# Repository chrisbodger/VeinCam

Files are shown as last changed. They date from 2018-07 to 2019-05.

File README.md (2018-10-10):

# Table Of Contents
1. [Feedback](#1-feedback)
2. [Progress Update](#2-progress-update)
3. [Audit Log](#3-audit-log)
4. [Concept of Operations](#4-concept-of-operations)
5. [Meeting Minutes](#5-meeting-minutes)
6. [Design Documents](#6-design-documents)

# 1. Feedback
A feedback form has been created for the interest of our stakeholders, should they wish to pass on any changes or improvements they believe to be prudent. The form can be found [here](https://goo.gl/forms/8cw5eWdaOY5C1jBo1).

Once the feedback has been received, an issue will be created within the GitHub repository for public viewing and tracking.  
**Any feedback is welcome.**

# 2. Progress Update
## October 9th

### Software

Implimented buttons into the HTML video streaming page, which trigger Flask/Python functions to set the camera parameters of brightness, contrast and saturation for the next frame. These buttons were designed to be large and use appropriate colours (red for lower, green for higher) in order to be intuative and intended for an educational audience. Following a meeting with the client after the testing, the stream is now shown in portrait rather than landscape to take advantage of the fact most users will be streaming to their personal devices in a portrait orientation, as well as being able to view someone's arm verticaly along the webpage.

All code had been uploaded into the software folder, including a complete image file which can be written to an SD card and used immediately with a Raspberry Pi and a PiCam (a method which has been tested and validated!). If the user does not have a PiJuice shield, minor adjustments must be made to app.py (see README.md in software folder or /home/pi/pistream in image for details).

#### A chronological work diary of software development throughout this project has also been added to the software folder.

### Audit 3 Presentation

The VeinCam was presented at our final Audit presentation during our tutorial timeslot. The final version was demonstrated to shadows and tutor. A draft of the poster to be presented next week was shown for feedback. The feedback given on the physical design, product functionality and overall presentation was very positive.

## Previous Progress Updates
* [August 1st](Progress-Updates/progress-update-2018-08-01.md)
* [August 7th](Progress-Updates/progress-update-2018-08-07.md)
* [August 11th](Progress-Updates/progress-update-2018-08-11.md)
* [August 18th](Progress-Updates/progress-update-2018-08-18.md)
* [August 25th](Progress-Updates/progress-update-2018-08-25.md)
* [September 5th](Progress-Updates/progress-update-2018-09-05.md)
* [September 25th](Progress-Updates/progress-update-2018-09-25.md)
* [October 2nd](Progress-Updates/progress-update-2018-10-02.md)

## Work Diary
For more detailed information on the work that has been completed please refer to the [work diary](docs/Team-Work-Diary.md)

# 3. Audit Log
Here we will have the information, results, and feedback to our audits, and will be presented in the following links (as they are created):

* Audit 1
* Audit 2
* Audit 3

Should our stakeholders wish to provide us with feedback, they can fill out a google survey in which we will action them appropriately as responses are presented to us.

# 4. Concept of Operations
Our Concept of Operations has undergone further iterations in recent weeks, primarily to the aims, scope and stakeholders of the project. We encourage any feedback on changes made.

The [Concept of Operations](docs/CONOPS.md) document can be found in our repository.

# 5. Meeting Minutes
Team meetings are scheduled two to three times a week with different stakeholders present. One meeting is internal with only the project team, one has the tutor and shadow team present, and one is with the project client. They are currently scheduled for the following times:
* Tuesday 10am (Tutor and Shadow Team)
* Wednesday 11pm (Project Team)
* Saturday 2pm (Project Client)

The wednesday and saturday meeting times may vary, depending on the availability of the team, and client.

Meeting Minutes can also be found in our repository:

## Last Meeting Minutes
* [September 29th](Meeting-Minutes/Meeting-Minutes-2018-09-29.md)

## Recent Meeting Minutes
* [September 5th](Meeting-Minutes/Meeting-Minutes-2018-09-05.md)  
* [September 15th](Meeting-Minutes/Meeting-Minutes-2018-09-15.md)
* [September 18th](Meeting-Minutes/Meeting-Minutes-2018-09-18.md)
* [September 19th](Meeting-Minutes/Meeting-Minutes-2018-09-19.md)
* [September 22nd](Meeting-Minutes/Meeting-Minutes-2018-09-22.md)

# 6. Design Documents
The design of the VeinCam will be presented here, once the ConOps has been approved, and progress/final designs are made available. the construction method of the device will also be presented here.

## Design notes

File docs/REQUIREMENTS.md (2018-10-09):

# Device Requirements and Design Specifications
Requirements were gathered from the client and refined into measurable specifications. The sets of both requirements and specifications should be considered evolutionary and may change through prototyping and testing.

## Requirements
Requirements have been developed through conversation with the project client resulting in a total of eight that would make the VeinCam a success.

| ID | Requirement |
| --- | --- |
| 1 | The device must be inexpensive compared to devices that have similar functions |
| 2 | The device must be handsfree |
| 3 | The device must be able to wirelessly connect to an external device with a screen |
| 4 | The device must be portable and mobile |
| 5 | The device must be simple to use |
| 6 | The device must be simple to construct |
| 7* | The device must display veins in as many use-cases as possible (e.g dark-skinned, tattooed, hairy) |

*Requirement 7 has elements of a stretch deliverable for the project.

## Specifications
The requirements were broken down into specifications that will provide validation for the project and can be verified through testing.

| ID | Specification | Metric | Benchmark |
| --- | --- | --- | --- |
| 1 | Total Cost | $ | <250 |
| 2.1 | Camera Focal Length | mm | 300-500 |
| 2.2 | Adjustable Set Height | mm | 300-500 |
| 2.3 | Handsfree Operation | min | >5 |
| 2.4 | Battery Life | min | >60 |
| 3.1 | Wireless Range | m | >1 |
| 3.2 | Stream Delay | ms | <1000 |
| 4 | Form Factor | mm | <150 x 90 x 70 |
| 5.1 | User Acceptance | % | >90 |
| 5.2 | Boot Time | s | <15 |
| 5.3 | OS Compatibility | # | >2 |
| 6.1 | Construction Steps | # | <5 |
| 6.2 | Construction Time | hrs | <2 |
| 7.1 | Automatic Contrast Adjustment (for ideal scenario) | % | >90 |
| 7.2 | Automatic Contrast Adjustment (for any complexion) | % | 80 |
| 7.3 | Automatic Contrast Adjustment (for high BMI/obesity) | % | 80 |
| 7.4 | Automatic Contrast Adjustment (for any amount of hair) | % | 80 |
| 7.5 | Automatic Contrast Adjustment (for tattooed area) | % | 80 |
| 7.6 | Visualise Vascular Blood Flow | % | 80 |

### Description
**1. Total Cost -** The total cost of all components necessary to construct the VeinCam

**2.1. Camera Focal Length -** The focal length of the camera used in the device. Must have an image in focus at a height where it will not interfere with the users.

**2.2. Adjustable Set Height -** The heights that the device can be held still without human interaction once set in the appropriate position (i.e within the camera focal length).

**2.3. Handsfree Operation -** The time that both the physical device and the software interface can operate without human interaction.

**2.4. Battery Life -** The amount of time the device can be used (while streaming) without needing to be plugged in to recharge.

**3.1. Wireless Range -** The range that the device is able to communicate wirelessly with an external device.

**3.2. Stream Delay -** The time taken for the recorded image to be processed and appear on the external device.

**4. Form Factor -** The size and shape of the device.

**5.1. User Acceptance -** The success rate that the device with users. Measured by user testing and feedback.

**5.2. Boot Time -** The time taken from switching the device on to an image being produced.

**5.3. OS Compatibility -** The number of operating systems that the device is compatible with.

*Note - More specifications may be generated for Requirement 5 after initial testing.*

**6.1. Construction Steps -** The number of steps needed to construct the device from scratch.

**6.2. Construction Time -** The time taken for an independent user to construct the device from scratch. To be tested by independent users.

**7.1-5. Automatic Contrast Adjustment (for various use cases) -** The success rate of the device to automatically adjust the contrast of the streamed image such that veins can be clearly seen, as judged by the user. Ideal situation is with a patient with a light complexion, against a white background. Other scenarios are where vein detection has been shown to be more difficult.

**7.6. Visualise Vascular Blood FLow -** The ability of the device to visualise real-time blood flow. Measured through success rate in user testing.

## Change Log

| Date | Section | Change | Justification |
| --- | --- | --- | --- |
| 26/9/18 | [Requirements](#requirements) | Remove sterilisation requirement and associated specifications: gapless case and surface roughness. | The device is to be used as an educational tool as opposed to a medical device. |
| 26/9/18 | [Requirements](#requirements) | The device does not need to improve venous puncture but still work for as many use cases as possible | As above. |
| 29/9/18 | [Specifications](#specifications) | Moved automatic contrast adjustment (ideal scenario) to requirement 7. | Testing has to be split up between device and user, this groups more user testing together. |

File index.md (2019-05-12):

<meta http-equiv="refresh" content="0; URL='http://chrisbodger.github.io/veincam2019'" />

<!--

<div style="text-align:center"><img src ="images/progress-images/test-stream-result-3-crop.png" /></div>

## What is the VeinCam
The VeinCam is an educational tool for vein visualisation that uses. It uses near infrared (nIR) light and a camera to stream a real-time image where veins can be easily seen. It is an open-source, build-it-yourself device so anyone who finds it useful will be able to construct it. There is a how-to guide of what materials to buy, how to put them together and the software to upload to get it all working.

## Current Stage
The VeinCam has been through a couple of prototypes to get to its current stage; which includes a functioning case, automatic image processing and manual controls on a streamed webpage. The current prototype looks absolutely stunning along side our favourite houseplant, Hugh!

<div style="text-align:center">
  <div class="row">
    <div class="column">
      <img src ="images/prototype/prototype-2.2-down.JPG" width="99%" height="99%">
    </div>
    <div class="column">
      <img src ="images/prototype/prototype-2.2-up.JPG" width="99%" height="99%">
    </div>
  </div>
  <div class="row">
    <div class="column">
      <img src ="Software/tutorial-images/iPhone Mockup1.png" width="99%" height="99%">
    </div>
    <div class="column">
      <img src ="Software/tutorial-images/iPhone Mockup2.png" width="99%" height="99%">
    </div>
  </div>
</div>

### To contribute or find out more check out the [GitHub site](https://github.com/chrisbodger/VeinCam) or email at <message2ben@gmail.com>
--!>

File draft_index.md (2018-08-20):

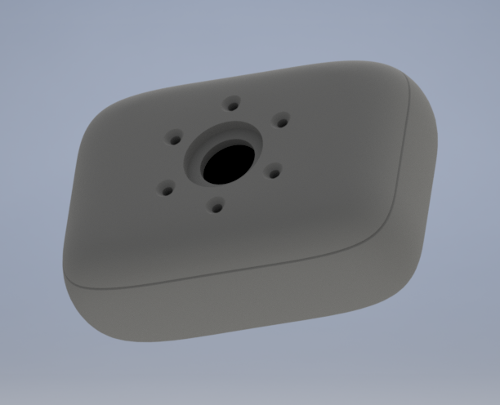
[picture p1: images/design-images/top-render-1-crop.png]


# What We're Doing
The main goal of our project is to ease patient discomfort. To do this we're using the VeinCam to make it easier for medical professionals to see veins in patients for superficial venous puncture.

# How We're Doing It
Not only are we making it easier, we're giving the power to them by developing an open-source DIY VeinCam and how-to guide so that anyone who needs one can build it themselves. We're providing a guide of what to buy, how to put it together and the software to upload to get it all working.

# When We're Done
This page will provide all the necessary downloads, links and resources that you'll need to construct a VeinCam yourself.

# Where We're At Now
Right now we're still working on getting it up and running but we have an image from our setup (as you can see we're using [Raspberry Pi](https://www.raspberrypi.org/) materials as they're available all over the world):

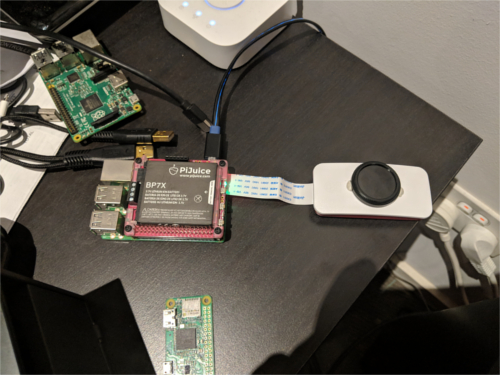
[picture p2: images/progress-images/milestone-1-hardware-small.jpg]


Our latest tests have been giving us some pretty good results as you can see below, but we're still working on adding automatic and manual contrast adjustment as well as a few other features.

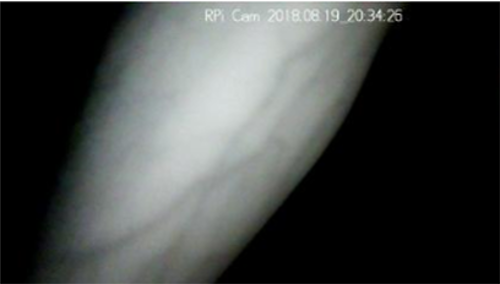
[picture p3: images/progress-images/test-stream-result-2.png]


## For more details check out our [GitHub site](https://github.com/chrisbodger/VeinCam)

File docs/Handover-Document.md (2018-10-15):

# Handover Document

This document is intended for the use of the Client Ben Healy, for future project teams who are continuing with this project in future semesters, and members of the public who wish to view the development and progress of the project summarised as of November 2018.

Feedback on this document, development of the project and other aspects of the project repository is always welcome and will be directed to the current project team FEEDBACK LINK HERE

Person's of interest for this document
'Client' - Ben Healy, medical student at the Australian National University
'Project Team'

## 1. Aims and purpose of this project
This project was started by the client who wished to develop an accessible and low-cost device that could be developed for the public for the purpose of enhanced vein visualisation using infra-red light - the VeinCam.
The client developed a preliminary prototype of the VeinCam based on the 2017 HackADAy Venenfinder project, and passed this prototype onto the project team to complete for their university course for further development of the device.
A full list of the project goals and stretch goals are in the [Concept of Operations document (ConOps)](/docs/CONOPS.md).

The project team is a group of four undergraduate ANU Engineering Students who completed a course which involved development of something as per the requirements and directions of the client. The course began in July 2018 and completed in November 2018.
A full list of the relevant stakeholders and their responsibilities at this stage of the project are
in the[ConOps](/docs/CONOPS.md).

The requirements developed by the project team and agreed upon by the client are listed in detail in the [Requirements](/docs/REQUIREMENTS.md)

## 2. Key development milestones and decisions
Decisions are summarised only in this document, with full dates, stakeholders involved and justifications in the [Decision Log](/docs/Decision-Log.md)
Main milestones are summarised in this document, with more details day-to-day activities in the [Team Work Diary](/docs/Team-Work-Diary.md)
Project updates have also been included in the repository every couple of weeks LINK HERE

### 2.1. Software development, key milestones and decisions
**Image Processing**
Currently, the VeinCam performs a histogram equilisaiton to "flatten" the contrast range of a taken image. This allows veins to not be washed out by higher contrast pixels of the image and as a result, veins appear are more prominently. There are several other image processing techniques that would be worth exploring to improve the VeinCam. These would include grayscaling, brightness/contrast threshold techniques, colour profiling and further histogram equilisation adjustment. Such examples can be found here:
https://hackaday.io/project/26158-assistance-system-for-vein-detection/details
https://hackaday.io/project/13329-yet-another-ir-vein-detector/details

**Manual Adjustment and Web Interface**
Following our final Audit, feedback was given on the ergonomics of the user web interface. It was mentioned that the buttons which manually adjust the brightness, contrast and saturation are not really suited beneath the image and having to continually scroll down is something that could be improved upon. A recommended solution for this would be a hidden sliding/three bar menu (as seen on many mobile websites) which would reveal the buttons to make adjustments to the stream.

The manual adjustment requires more manual testing to see what ranges and what parameters are best to adjust. The level of equalisation was also a parameter that was to be modified but the active decision was made to only adjust brightness, contrast and saturation as a proof of concept. There are many more possible parameters to adjust, including the levels of colour/brightness thresholds and strength of other imaging techniques, as well as being able to switch the image techniques being shown on the stream. 

### 2.2. Hardware development, key milestones and decisions
**Case**
The final case that we printed before the end of the project had some slight errors - namely misaligned buttons and LED passthroughs. We were able to overcome this defects for testing and demonstration purposes however. The repository contains v2.3 that includes these changes, and needs to be printed and tested going forward.

A proper mounting and securing solution needs to be designed for the Raspberry Pi, to prevent it from falling out of the case was it is being used. Currently, we are using foam cut-outs that were lodged in between the Pi and the case and that secured it quite well, though its not very permanent.

Because of the cut-outs, the device case is not very resistant to any sort of fluid. Some method needs to be implemented to plug these holes temporarily (a charging port cover for example), or permanently (LED indicator passthroughs). Transparent filament could be used and printed in situ to create a light channel for the LED lights and make them easier to see from the external of that case (a traditional method for indicator lights in devices), or use some other material like clear acrylic sheet and stuff it into the holes. Both options worth exploring.

The buttons are complete and should fit snuggly into the button holes.

**Surface Finish**
We were not able to perform any post-printing methods to clean up the prints. We were left with bumps and misplaced filament and an excess of support material to be removed still. This could be potentially detrimental as it leaves the case to be able to pick up dirt and grime and dirty up the case and potentially encourage bacterial growth given the number to small crevices within the surface. An idea that was had was to sand down the external surfaces with a fine grit to smooth it down, and adjust the print settings for the support material. other options could be utilised, depending on how the case is made.

In addition, not many people may have access to 3D printers. It would be worth looking into alternative case ideas, such as cardboard (like the Google Cardboard or Nintendo Labo), or acrylic sheet.

**IR LED Array**
The LED array was always intended to have its own custom PCB, to make it easier to manufacture as it would remove some variances of soldering the LEDS incorrectly and still fitting within our case design.

**Pi Zero Platform**
Given the resources used while the camera stream was operating, it may be possible to downsize the Pi 3 to a Pi Zero. This could potentially decrease the battery usage, and make appropriate use of the available resources, instead of having so much not utilised. This would still need to be tested of course, something we wished to at least attempt. But we did not have any interfacing methods to at least connect the Pi to a network, let alone connect the camera module to the Pi Zero.

The bottleneck with both Raspberry Pis would be the number of devices connected via the hotspot software. We experienced a lockup of the device when more than eight devices tried to connect during our presentation. However, given that only one device should be connected the the Pi at any given time, this should not be an issue going forward.

### 2.3. Governance and project aims/scope, key milestones and decisions

## 3. Future of the Project
Ideas about the future of include things that this project team has attempted and needs improvement on, things which were
outside the scope of the project (either from the beginning, or later on in the project).
These ideas were developed from the project team, with external advice and feedback from the client.
Testing that was completed by the client just prior to the end of the project is summarised in [this document](/Resources/Client-Feedback-VeinCam-Testing.md).

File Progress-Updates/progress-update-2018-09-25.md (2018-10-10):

## September 25th
Several weeks have gone by since the last update, and theres much to talk about:

### Hardware
We are up to case version 2.2, that incorporates a smaller form factor and better ergonomics. Unfortunately these past few weeks have not been able to produce a successful print of the new case. We believe that this will be the final iteration of the case.

The only variation to the case that may happen is testing into a different LED configuration. the aim is to attempt to achieve a better contrast of skin and veins, and hope to achieve deeper skin penetration to visualise veins on people who have a higher BMI. This is still on going but we hope to have a clear idea by the end of this week.

### Software
The software currently works to automatically start up on boot up; initialising the wireless access point for external connections and starting the web stream to an external device. It has been noted that the wireless access point fails to start sometimes, making it difficult to connect to externally. This will be looked into as it is believed that there is other software that may be interfering with the hosting software and blocking it from starting.

Aside from this, some manual controls will be implemented to the hosting web page for better control over the software processing and image input.

### Governance and Bureaucratic Issues
Over the source of the mid semester teaching break the team was in contact with a variety of sources to discuss the purpose of the device and how that impacts the how we distribute information about the device. Through much discussion, the group decided the best path for the future of the project would be to advertise the device as an educational tool, assisting with teaching about veins and educating the public for informed consent of medical procedures.

Additionally, through correspondence with legal services and the ANU Human Ethics Committee, the group became aware that initial human testing of the device would not be able to be completed at this stage of the project as human ethics approval is necessary to do testing. This provides some roadblocks for the development of the device as the group is not able to determine how the device needs to be improved for optimal practical use. As such, the aims and scope of the project were modified slightly.

Going forward, the group will be finishing up with tutorial documents on how to build the device, documents for conducting future testing, and acting on feedback from the client on the functioning of the device. The group is also developing designs for the poster to present the device at the closure of this project.

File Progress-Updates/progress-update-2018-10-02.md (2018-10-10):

## October 2nd
The client has recieved our second complete prototype to take and provide feedback on based on their use.
Photos of the prototype can be found in the 'images' folder, and a user instructions manual above in the main respository.  

### Hardware
At long last, case version 2.2 finally completed a full successful print. No changes were made to the LED configuration after testing of LEDS with differing wavelengths (840 vs 940nm) proved to not improve performance of viewing veins. The case was assembled however the mounts, charging port and button hole placement was found to be all out of place (less so than previous iterations). This will be a major focus for the final design.

Instead, firm packing foam was used to hold the components in place and align the PiJuice charging port with the charging hole cutout of the case. Makeshift buttons were made to turn the system on and off without having to open the case. The camera cable was replaced as it had been found to have been damaged during testing; a discovery made when the camera failed to load at the very last minute prior to client handover. This was replaced, tested and found to have resolved the issue.

### Software
A first attempt of a handover to the client with a makeshift prototype was made on Saturday, however the streaming web page would not load. This was found to have been due to an imcomplete line of code left in the script, due to having not saved the changes made. As a result, the main script would not complile. This was quickly resolved, but to ensure operational integrity during the client's testing, the system's operating system was wiped and reloaded with only the necessary files. This was performed to ensure there were no conflicting files that could cause issues during client use.

Variable control using Flask via HTML is still in development, to be ready for the final version.

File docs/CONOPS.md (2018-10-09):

# Concept of Operations

Version 1.1 Signed-off by stakeholders as of 9/10/2018.

## Table of Contents
* [Project Vision](#project-vision)
  * [Value Proposition](#value-proposition)
  * [Project Scope](#project-scope)
  * [Project Comparison](#project-comparison)
* [Stakeholders](#stakeholders)
  * [Project Team](#project-team)
  * [Project Client](#project-client)
  * [Shadow Team](#shadow-team)
  * [Course Tutor](#course-tutor)
  * [Course Convenor](#course-convenor)
  * [Users](#users)
* [Resources](#resources)
  * [Funding](#funding)
  * [Tools](#tools)
* [Project Management](#project-management)
  * [Deliverables](#deliverables)
  * [Milestones](#milestones)
  * [Audit Goals](#audit-goals)
  * [Timelines](#timelines)
  * [Work Breakdown Structure](#work-breakdown-structure)
  * [Decision Making and Conflict Resolution](#decision-making-and-conflict-resolution)
* [Risk Analysis](#risk-analysis)
  * [Safety Risk Analysis](#safety-risk-analysis)
* [References](#references)
* [Change Log](#change-log)

---

## Project Vision
The VeinCam is based on the [Venenfinder project](https://hackaday.io/project/26158-assistance-system-for-vein-detection) submitted during the 2017 HackADay event. The goal was to create an affordable device that produces a clear image of a suitable vein for superficial venous puncture, a procedure that is a requirement for patient blood testing and the delivery of external drug administration. However the goal of this project is to extend the customer base to educators and students while maintaining affordability and accessibility.

### Value Proposition
Our VeinCam device will help students better understand venous sites by augmenting visualisation of upper limb veins. It will provide students with a better understanding of venous sites around the body compared to an image or model. The VeinCam is not intended for use as a medical device.
### Project Scope
The project aims to greatly extend and refine what was achieved in the Venenfinder HackADay project; automating and adding to some of the functionality while remaining cost effective.

The device should be portable and widely accessible. Veins will be illuminated using near-infrared light and the scattering from this light detected by a Raspberry Pi device equipped with a Pi noIR module. The project will be looking exclusively looking at using a Raspberry Pi as the basis for the device as has been suggested by the client due to the Pi platform being available internationally as a well established product for such uses. Additionally the Pi system has a rich set of add-on devices that support development of a vein camera.

The software from the Venenfinder project will be heavily modified, incorporating intelligent OpenCV scripts to perform automatic adjustments to the lighting and contrast settings. Manual adjustments will also be implemented in order to get the best possible image in any use case.

### Project Comparison
As this project is building on what was achieved by the Venenfinder project, it is worth noting what is being added.

#### Feature Summary
| Venenfinder | VeinCam | Future Development |
| :---: | :---: | :---: |
| IR Illumination | IR Illumination | Various Skin Conditions |
| Camera | Camera | Vein Identification |
| Manual Brightness Adjustment | Auto Brightness Adjustment | Smaller Platform |
| Manual Contrast Adjustment | Auto Contrast Adjustment | Extended Battery Life |
| Manual IR Adjustment | Auto IR Adjustment | . |
| . | Wireless | . |
| . | Portable | . |
| . | Smaller Footprint | . |
| . | AI Image Processing | . |

#### Venenfinder Features
The Venenfinder team were able to produce a device that was able to use a near-Infrared light to illuminate a patient's veins. The device uses a Raspberry Pi, a noIR camera module, and a 3x3 array of IR LEDs. Brightness of the LEDs and contrast ratios were manually adjusted using potentiometers to adjust intercepted voltages between the array and the RPi. The camera image is then streamed to a secondary web enabled device through a web browser. This method works for devices ranging from mobile phones to desktop PCs.  Unfortunately the device was quite large and bulky, resulting in the need for an external power source.

#### VeinCam Core Features
The VeinCam project hopes to utilise similar hardware to the Venenfinder project (Raspberry Pi, PiCam, IR LEDs) and extend the software's capabilities to automatically adjust the infrared light filtration, brightness and contrast to produce the clearest image possible with limited manual adjustment.

Further adding to the Venenfinder project; the aim is to produce a device that is battery powered, completely wireless and to reduce the size of the device to be comfortably held in one hand. Being a wireless device, we need to ensure the device is as power efficient as possible and does not require recharging more than absolutely necessary. As part of the new housing for the device, a mounting system will be integrated, and a mount be devised for hands-free use. 

#### VeinCam Testing and Future Development Plans
Once the core device has reached the prototype stage in-house testing will be completed on the device to determine its functionality and improve the technical aspects. The device will also be informally tested as a proof-of-concept.

Formally conducting testing requires ethics approval which is outside the scope of this project. Examining the formal testing processes will provide the project pathways to continue into the future. 
To formally verify and validate the device extensive testing will need to be completed on varying skin conditions and appearances such as: complexion, hairy, tattooed areas and other skin abnormalities (barring skin irritations such as rash and infection). The prototype will also be tested with potential users of the system to ensure that it functions acceptably; feedback will be taken to revise the prototype. Similarly potential users will be asked to construct the VeinCam so it can be ensured that the device will be independently constructible as necessary if the device is successful. 

Also requiring further investigation and implementation; the device may be able to be shrunk to a smaller platform, such as the Raspberry Pi Zero. This would allow for the device to become a lot cheaper to build, reducing the size to something that fits into the palm of your hand, and be able to conserve more power. Implementations and performance would need to be investigated, as the Pi Zero may not be able to process the video stream as effectively as its larger counterpart.

---

## Stakeholders
The following groups have been identified as stakeholders for this project:

| Stakeholder | Project Interaction |
| --- | --- |
| Project Team | Produces the Project Output and actions constructive feedback from other stakeholders |
| Project Client | Provides feedback on project progress |
| Shadow Team | Observes the Project and provides constructive feedback |
| Course Tutor | Provides feedback on project progress |
| Course Convenor | Provides feedback on project progress |

### Project Team
The project team consists of four undergraduate engineers who each have roles as point people in the project. All members of the team should be present to support each other in whatever way is necessary to complete tasks and better the project. The designated roles give each member a lead position, they are responsible for their sections and as such if any questions from external stakeholders specifically address a section of the project they are the member to contact.

| Name | Role | Email |
| --- | --- | --- |
| Christopher Bodger | Lead Hardware Engineer | u5395595@anu.edu.au |
| Alexander Ollman | Lead Programmer | u5826805@anu.edu.au |
| Stephanie Pratt | Stakeholder Liaison, Lead Researcher | u5822871@anu.edu.au |
| Jonathan McPhail | Secretary | u5351489@anu.edu.au |

#### Responsibilities of the project team to the project
* Fulfil the tasks assigned by the team within the desired time frame to the best of their ability.
* Communicate the progress and setbacks of their tasks regularly with the team.
* Commit to regularly attending scheduled meetings, or otherwise remain up to date with meeting minutes and contributing to meeting agendas.

##### Responsibilities of the Lead Hardware Engineer
* Manage and design the hardware of the device.
* Design and test the layout and chassis of the device.
* Manufacture the prototype device.

##### Responsibilities of the Lead Programmer
* Design the code for the device to meet deliverables and requirements.

##### Responsibilities of the Stakeholder Liaison
* Be the point of contact for general communication between stakeholders.
* Organise meetings with the client and other stakeholders when necessary.

##### Responsibilities of the Lead Researcher
* Perform research required to strengthen the project.
* Delegate research when necessary to other team members.

##### Responsibilities of the Secretary
* Maintain the repository and landing page.
  * Including all documentation and meeting agendas/minutes.

**To reiterate these roles show who questions should be directed to and are not indicative of workload.**

### Project Client
Ben Healey (message2ben@gmail.com)

Ben is medical student at the ANU and an employee of ACT Health. He personally began this project using pointers from open source projects such as the 2017 HackADay project and the Venenfinder project, to develop an affordable vein imaging device.

#### Responsibilities of the project team to the client
* Design a device to meet the established baseline requirements that the client has presented.
* Keep the client regularly updated with milestones and setbacks.

#### Responsibilities of the client to the project
* Provide information and requirements about the project to the team.
* Respond to communications on a regular basis.
* Be present and prepared at scheduled meetings.

### Shadow Team
ANU undergraduate engineering students, tasked with reviewing this project to provide an external viewpoint on the outputs and governance of the project.

| Name | Email |
| --- | --- |
| Ethan Stanbury | u6048363@anu.edu.au |
| Jiacong Zhao | u6029134@anu.edu.au |
| Jiarui Wang | u5879960@anu.edu.au |
| Liam Highmore | u5563628@anu.edu.au |
| Namisha Chabbra | u5644087@anu.edu.au |
| Yifei Ren | u6137095@anu.edu.au |

#### Responsibilities of the project team to the shadow team
* Provide shadows access to all information surrounding the project, including repositories, documentation and relevant communications.  This information should be up-to-date and presented appropriately.
* Be open to feedback from all channels from shadows, and act on feedback appropriately.

#### Responsibilities of the shadow team to the project
* Remain up-to-date with the activities, outputs and governance of the project through information that is supplied to them.
* Commit to providing constructive, accurate and actionable feedback to the project through the pathways provided to them: including formal audit feedback, as well as verbal feedback in tutorial sessions and through the feedback forms supplied.

### Course Tutor
Jenny Simmons (jenny.simmons@anu.edu.au)

ANU ENGN4221 course tutor for Semester 2 2018. Tasked with formally organising and directing weekly tutorial sessions where the project is planned, presented and reflected upon.

#### Responsibilities of the project team to the course tutor
* Provide the tutor access to all information surrounding the project, including repositories, documentation and relevant communications. This information should be up-to-date and presented appropriately.
* Be open to feedback from the tutor, and act on feedback from all channels appropriately.
* Be present and prepared at all weekly tutorials (Tuesday 10-12), appropriate to the activity of the tutorial that week.
* Be informed of the structure of the course and related assessment milestones as established by the course convenor.
* Be prepared to submit assessments, and be open to grades and discussion of grades with the course tutor.

#### Responsibilities of the course tutor to the project
* Be present and prepared to lead the tutorial each week, appropriate to the activity of the tutorial, and remain up-to-date with the progress of the project.
* To a reasonable extent, assist the project team with the progress of the project, including answering relevant and reasonable questions, and providing constructive, actionable and accurate feedback, particularly at times of project audits and during tutorial sessions.
* Reply to correspondence (email) in a timely fashion, and grade formal assignments fairly and appropriate to the quality of the project.

### Course Convenor
Chris Browne (chris.browne@anu.edu.au)

ANU ENGN4221 course convenor for Semester 2 2018. The course convenor is the overall authority and organiser for this course, and hence the projects that run through this course.

#### Responsibilities of the project team to the course convenor
* Same as those applying to the course tutor.

#### Responsibilities of the course convenor to the project
* Same as the course tutor with the addition of:
* Organise the course appropriate to the desired outcomes and be receptive to feedback regarding this structure. Information regarding the structure and assessment milestones of the course should be available to students within a reasonable timeframe.

### Users
Members of the public, particularly students and educators who wish to utilse the device for educational purposes. 

#### Responsibilities of the project team to the users
* Provide members of the public access to information that pertains to all aspects of the project.
* Design a device that, at minimum, must not endanger the safety of potential users.
* To the best of their ability, provide the public with the information to design an affordable device that can image the veins of a person.

#### Responsibilities of the users to the project
* Members of the public have little steadfast responsibility to the project team.
* Ideally, members of the public will provide feedback on the function of the device during requirements analysis or testing.

---

## Resources
### Funding
At most, the project should cost no more than the $400 proposed in the design brief. This will include the hardware and components necessary.

Ideally, the project should cost less than this. A [Bill of Materials](#bill-of-materials) with associated can be seen below. This is likely to be updated as the prototype is developed and costs are encountered. All additional proposed costs will be agreed upon by key stakeholders before purchase.

### Tools

Tools likely to be used throughout this project include:
- Soldering Iron
- 3D Printer
- Laser Cutter
- Dremel
- Screwdriver, screws, nuts and bolts.

All safety precautions outlined by the ANU Makerspace's Terms and Conditions will be followed during the use of instrument or tool, regardless of where and how it is used. A safety risk analysis has been performed at the bottom of this document.

#### Project Administration
* GitHub
* GitHub Pages
* Google Drive
* Facebook Messenger Platform

#### Manufacturing and Testing
* Ian Ross Design Studio
* ANU Makerspace

##### Bill of Materials
An initial Bill of Materials has been drafted below of what we expect the project to cost.

| Component | Cost (AUD) | Supplied By Client |
| --- | :---: | :---: |
| Raspberry Pi 3 | $65 | Y |
| Raspberry PiCam | $50 | Y |
| Raspberry Pi Battery Module | $90 | Y |
| 10 x 840nm near-Infrared LEDs | $22 | N |
| 10 x 220 Ohm Resistors | $5 | N |
| 8 x Disk Neodymium Magnets | $5 | N |
| 3 x Cuboid Neodymium Magnets | $4.50 | N |
| IR Filter | $10 | Y |
| 1kg Filament | $34 | N |
| Total | $240 |   |

Please note these pricings are indicative and can change with the market. It is also worth noting that the client was kind enough to provide most of the hardware, as we can see in the table. This means the required costs during our development will be minimal to purchase the remaining inexpensive components.

#### Programming
* Source code from the Venenfinder HackADay project has been utilised, as it achieves close to the client's desired deliverable. This code will then be modified to achieve the client's desired features, including auto-vein focus.

---

## Project Management
### Deliverables
The initial deliverables are as follows:  

#### Baseline Deliverables
* Configure device based on Venenfinder to be able to automatically adjust contrast.
* Design and manufacture a prototype chassis to house Pi modules to allow for handsfree, real-time visualization.
* Produce a "how to build" and "how to use" guides for the device.
* Perform initial in-house testing on the device itself (not formal user-testing).

#### Stretch Deliverables
In order of priority.
* Implement manual controls for image adjustment.
* Compile user feedback on the construction and use of the device (based on the written guides).
* Optimise for different use-case scenarios (e.g. tattooed skin, dark skin).
* Design or source an appropriate hands free stand to mount the device.
* Optimise device to visualise blood flow to identify best candidate vein

#### Ultra-Stretch Deliverables or Future Project Aims
* Configure device to run off of Pi Zero module
  * Offload image processing to secondary device

### Milestones
Further detail on the optimisation of milestones and design aims of the prototype are detailed in the Requirements document.

#### Milestone 1
Construct functional prototype based off of Venenfinder design.

#### Milestone 2
Configure software to automate brightness and contrast of vein visualisation, and design hardware to reduce product's form factor.

#### Milestone 3
Initial AutoCAD design of 3D-printable chassis, maximize automatic focus and brightness to optimise software enhancement of the captured raw image for clear image definition.

#### Milestone 4
Final AutoCAD design and phyiscal print-out of chassis, accompanying web/smartphone appication to display camera image, contain adjustable settings, and optimise battery life and charging scenario.

### Audit Goals
#### Audit 1
* Complete ConOps Version 1

#### Audit 2
* Update ConOps to Version 2
* Complete requirements analysis
* Reach Milestone 2

#### Audit 3
* Achieve Milestone 3/4 with accompanying verification and validation

Milestones are subject to change as the project evolves.

### Timelines
An [indicative schedule](https://docs.google.com/spreadsheets/d/1nfNqFCF2ieP5CyVmqDSeZ3oXegxcCG4hojdd6fMcq9Y/edit?usp=sharing) has been drafted for the project.

### Work Breakdown Structure
1. Requirements Analysis  
   1.1. Review PoC  
   1.2. Perform risk analysis  
   1.3. Brainstorm requirements (in-house)  
   1.4. Develop requirements with client  
   1.5. Finalise requirements  
2. Prototyping  
   2.1. Design hardware  
   2.2. Manufacture and construct hardware  
   2.3. Design baseline software  
   2.4. Integrate software  
   2.5. Update software with stretch deliverables
3. Validation & Verification  
   3.1. Test prototype in-house  
   3.2. Conduct performance review  
4. Documentation  
   4.1. Write ConOps v1  
   4.2. Update ConOps v2  
   4.3. Create "How-to" guide  
   4.4. Create poster  
   4.5. Organise repository  

### Decision Making and Conflict Resolution
Decision making will be by consensus in consultation with the client. When consensus cannot be reached the project team will seek advice from other stakeholders depending on the nature of the decision. For further detail please refer to the [Decision Log](/docs/Decision-Log.md).

---

## Risk Analysis
All risk analysis performed throughout this project will be in accordance to the Australian and New Zealand Industry Standard AS/NZS 4360:2004.

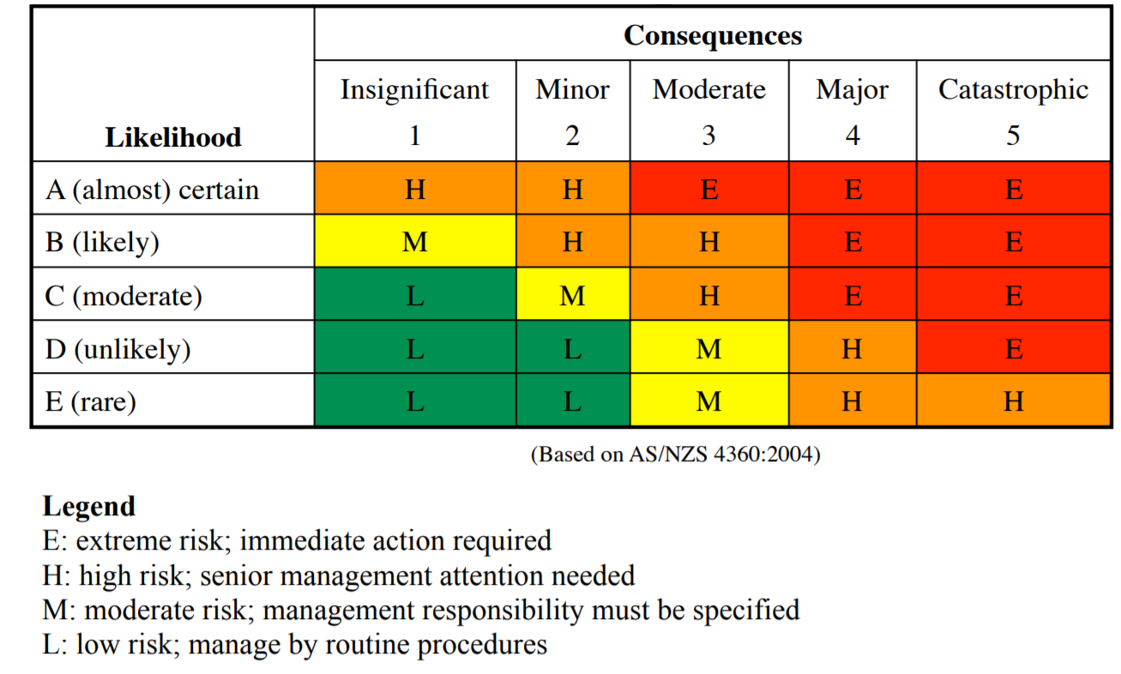
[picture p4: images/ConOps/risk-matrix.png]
Risk Matrix


Potential risks to the success of the project have been brainstormed in order to understand them and mitigate either their severity or likelihood.

| Risk | Consequences | Likelihood | Severity | Mitigation |
| :---: | :---: | :---: | :---: | :---: |
| Not clearly understanding or defining client's requirements for the project. | Product does not meet client requirements, client dissatisfied, requires re-doing work, going over budget and schedule to redesign | D | 3 | Maintain regular contact with client regarding progress and milestone completion. |
| Not defining scope of project and setting clear and achievable milestones. | No clear definition of project progress, feature creep over time results in lack of physical product, no clear "stopping point" for project or completed product, client dissatisifed, product does not meet customer requirements, likely to be over-budget. | C | 3 | Defining scope early and ensuring we stick to milestones and their respective outputs to ensure we do not deviate on a project tangent. |
| Device cannot be utilized as a medical device due to not meeting medical certification criteria. | Unable to deliver product to medical professionals, which is client's ultimate goal for the project. | C | 2 | Ensure client is aware of potential certification issues, and that they verify during development whether the device can be used with and/or without the medical classification. |

### Safety Risk Analysis
In developing the prototype there is a chance of injury, similar to above these risks have been listed and steps taken to mitigate their severity or likelihood.

| Risk | Consequences | Likelihood | Severity | Mitigation |
| :---: | :---: | :---: | :---: | :---: |
| Personal harm whilst using listed tools (incl. burns, shocks, cuts) | Pain, discomfort and possible medical attention. | D | 3 | Ensuring all team members are familiar with the safety training of the ANU Makerspace/Engineering workshop, supervision by one other team member when using potentially dangerous tools. |
| Damage to Hardware due to physical impact or electrostatic discharge (ESD) | Loss of data, hardware faliure, schedule delays to order and replace damaged hardware. | E | 4 | Ensuring hardware is never placed in an area where it is likely to be damaged, always in full visible sight. Observing proper ESD safety techniques, such as regularly grounding ourselves and only contacting circuitry by edges. |

---

## References
[Venenfinder Github](https://github.com/Myrijam/Venenfinder)

[Venenfinder HackAThon Page](https://hackaday.io/project/26158-assistance-system-for-vein-detection)

---

## Change Log

| Version | Section | Change | Justification |
| --- | --- | --- | --- |
| 1.1 | [Project Vision](#project-vision) | Adjust project vision to create an educational device. | There are a lot of responsibilities for a medical device manufacturer. Developing the VeinCam for an educational purpose removes these responsibilities. |
| 1.1 | [Project Management](#project-management) | Added how-to build and how-to use guides, and device testing to baseline deliverables. | Missing from previous deliverables and necessary for open-source construction and verification. |
| 1.1 | [Project Management](#project-management) | Added manual adjustment and user feedback deliverables. | Considered more important than the other stretch deliverables as it will enhance the user experience and is more achievable. Testing will provide points for the project to move forward. |
| 1.1 | [WBS](#work-breakdown-structure) | Removed testing with users. | No longer falls within the scope of the project and would require ethics approval. |
| 1.1 | Value proposition, VeinCam testing, Users and Baseline deliverables | Formally stated not intended as a medical device. Making it clear testing is only in-house and any further testing is detailed only for future development of the project. Adjustment of users to specify students and educators as per the revised purpose of the device. | As per changes recommended by the client to align with re-purposing of the device for educational purposes. |

This Project is licensed under the Creative Commons license.

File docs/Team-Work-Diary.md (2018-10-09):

# ENGN4221 VeinCam Project Team Work Diary

Instruction: Team members to add progress of assigned tasks, including date of update and team member/s involved.

## Hardware and Software Activities

Progress from start of project as at 15/08/2018
* Assembled the hardware into the proposed configuration
* Installed and prepared the operating system as per the VeinCam Tutorial (Install OS, OpenCV and PaspAP softwares).
* Performed testing of the hardware with sample code provided by the Raspberry Pi documentation.

17/08/2018
* Alex researching into the implementation of manual software controls in a HTML web page space - intermediary step to automatic controls. Rudimentary control methods in place, yet to make them actionable.
* Chris designing an enclosure for the device and components using CAD software. Several concepts in mind, looking for a compact, ergonomic form factor.

18/08/2018
* Preliminary design of the case presented to the client. He was overall happy with the design as it stands. will continue to work on to add further features to accommodate the Pi device.

22/08/2018
* The first prototype (v1.0) case design ready to be printed. Chris will start the print in the makerspace overnight and will need to picked up the following day.

23/08/2018

**Hardware**
* Case v1.0 printed successfully, with a few minor defects. The simple supports for the Pi were easy to break, and most of the support material did not come away easily. Case v1.1 should be started today, hopefully to be picked up tomorrow for ANU Open Day. V1.1 brings stronger Pi supports, a more flush interface with the lid, enlarged openings for the IR LEDs, and a 180 degree reorientation when printing. this reorientation will generate more support material, but will hopefulle make for an easier clean up post print.
* The case shell was cleaned as best as possible and was determined to be too large for small hands. v2.0 has begun to address this, cutting the size down by almost 10mm all round. a proper mounting solution for the LED array will be embedded into the case lid as well, when the LED array has been constructed and finalised. further design improvementments to be implemented after our weekly meeting with the client.

**Software**
* Scrapping the manual controls for the moment. Focussed more on the image processing and getting a clear, defined image of veins for Open Day. Constructed an script using OpenCV which would capture an image, perform a histogram equalisation of the image, and then feed the equalised image into a stream. The next major goal will be to parse this video stream into a web page that can be accessed by any external device.

27/08/2018

**Hardware**
* Alex constructed the LED array to be placed in the newly 3D-printed v1.1 enclosure for a full demonstration of our first complete prototype during the Audit 2 presentation.

**Presentation**
* Steph presented our project to the tutors and tutorial group, including our shadow team. We received great feedback and plenty of questions, which gave us an idea of how others external to the group viewed our progress. The topics of commercialisation and hygiene (sterilizing our product for hospital environments) were raised and gave the group plenty to think about when considering the final design. The prototype demonstration went very well.

30/08/2018

**Hardware**
* Version 2.0 of the chassis has been completed, and printed has started on it for completion and assessment over the coming days. further changes are expected, and hopefully they will be minor so that it can be handed over to the client for testing, pending completion of the software.

03/09/2018 - 04/09/2018

**Software**
* Solved issue of sending processed images to stream by scrapping old streaming code and instead using Flask (based on code by Miguel Grinberg at https://blog.miguelgrinberg.com/post/video-streaming-with-flask). Device can now stream live images to WLAN localhost at 60fps, meaning any device can connect to the network outputted by the RasPi and view the stream.
* After many hours, we also managed to get the streaming script to run on startup. This ensures that all a user has to do is press the power button and the device will begin streaming (after 30 second boot time) to its localhost address.
* Cleaned up HTML code, which now displays correct fonts and current RasPi temperature (for testing purposes).
* Currently working on displaying Battery percentage on stream web page and improving the image processing capabilities.

06/09/2018 Joey
* v2.1 of the chassis, including buttons and both shell and lid started (speed set to 50mm/s to ensure clean print)

18/09/2018 Chris
Retrospective Recount of the last two weeks:
* Attempted several times to print case v2.1, with no success. Attempts would either fail to print entirely, or would not print cleanly, and leaving features malformed.
* Due to so much wastage from the failed prints, a new roll of filament was ordered 7/9/18. The replacement roll arrived 14/9/18.
* v2.2 of the chassis was created, altering the shape to take on more of an hourglass, in an effort to make the case easier to hold by the ends. Currently, this revision is being printed, and seems to be printing well. smaller features yet to be printed to see if this remains the same.

* Software completed the autostart and initialisation procedures for the web stream and image processing. Currently, it outputs the processed image at a reasonably high framerate for its intended use. The webpage however has an issue initialising the stream in a timely manner (upwards of 30 seconds) and the Wireless connectivity fails to initiate on some occurrences. These will hopefully be explored in the coming weeks.

25/09/2018 Chris
Started work on an alternative LED array to try and achieve deep vein visualisation. An array of both 850nm and 940nm has been laid out but yet to be tested. The case lid has been slightly altered to be able to house 12 LEDs in preparation of success.

Printing the case has been continually failed since last term, regardless of the printer and variation of settings. We will need to speak to one of the technicians on how to successfully print the case.

29/09/2018 Chris, Alex
After the failure of the device during handover to the client. the Software Team agreed that it would be best to rebuild the operating system, as the behaviours presented (failure to broadcast a visible wifi, failure to initiate the camera web stream) could not be pinpointed to any one thing. Despite the time consumption to prepare the operating system, it would have taken even more time to fix these errors.

The operating system was prepared in full by end of day.

01/10/2018 Chris, Alex
The script runs consistently and reliably, along with the wifi connectivity. we initially had issues starting the script as it was worked into the system profile and the profile was not being sourced, thus the camera script not starting. The system was told to boot into its Command Line Interface, and switched back to GUI mode before we noticed the script running on start up. as of that evening, after multiple reboots and shut downs, the device continued to work as intended, and is ready for handover on 02/10/2018. A backup of the system was taken in case something were to go wrong.

## Documentation, Research, Meetings and other Governance Activities

Progress from start of project as at 15/8/18
* First draft of ConOps Complete not yet signed off from stakeholders
* First draft of Requirements complete, awaiting feedback from Client
* Work breakdown structure and corresponding Gantt Chart constructed
* 7 meetings so far, all minutes available on repository, 4 group meetings (every Wednesday 11am) and 3 client meetings (Saturdays 2pm weekly as needed)
* Landing page draft complete
* First Project Audit complete (7/8/18), feedback received and action tasks assigned accordingly
* Steph and Joey currently assigned research
* Decision log created and first contribution added

15/8/18 Steph, Alex, Joey
* Group meeting conducted. Minutes recorded.

15/8/18 Steph
* Feedback from client for conops reviewed and ConOps updated accordingly
* feedback from client for requirements received

16/8/18 Steph, Joey
* Issues added, Joey to address client feedback requirements
  * Feedback addressed, awaiting confirmation at client meeting.

16/8/18 Joey
* Decision Making/Conflict Resolution added to ConOps and Decision Log.
  * Column "Stakeholders Involved" added to decision log.

20/8/18 Joey
* Landing page changed over to a more public friendly style

21/8/18 Steph
* Reviewed email from Client regarding sourcing LEDs - pass this on to the team
* Received confirmation from Convenor regarding Open Day presenting
* Requested Client permission for Open Day presenting

22/8/18 Steph
* Reviewed email from Client confirming permission for Open Day presenting
* Created resources file in the Git to store info about purchasing new hardware
* Emailed Convenor about Open Day
* Client passed on that he has linked veincam.org to the Github site

22/8/18 Joey
* Font-style of landing page adjuest to client's original type.
* ConOps contract created.
* Initial market research performed, at least four competitors found.
* Landing page content updated.
* Work diary link added to readme.
* Added small section in testing to the ConOps.

7/9/18 Steph
*  Purchase log created

24/8/18 Steph
* Sent microgrant application to Course convenor
* Completed research regarding medical device classification, regulation and marketing. Will upload this onto Git in the next week
* Basic draft of audit 2 presentation started

25/8/18 ALL project team
* Open day presentation and user testing
* Signoff of Conops and requirements by team and client

27/8/18 Steph
* Sent conops agreement to project tutor for signoff - received signoff. Updated ConOps for Version 1.0 with all stakeholders signoff
* Received acceptance of microgrant ($40) from course convenor.

27/8/18 Joey
* Updated the public landing page with a few new images and current state of the project.

27/8/18 Alex and Chris
* Discussion regarding next phase of hardware and software development, including defining and finalising modifications to the v2.0 design of the enclosure.

28/8/18 Steph
* Created user feedback document in resources file of repository
* Updated user feedback with preliminary results from open day 25/8/18
* Created research document, starting compiling research

4/9/18 Joey
* Created initial site design and architecture,
* Created site pages to expand the website. Not yet complete.

11/9/18 Steph
* Meeting with ANUSA Lawyer to discuss liability issues
* Email sent to TGA regarding medical device definition and compliance
* Research done on human ethics

12/9/18 Steph
* Email sent to technology transfer office to make booking
* Email sent to ANU human ethics committee regarding need to ethics approval
* Appointment made with ANU Technology Transfer Office

14/9/18 Joey
* Initial testing documents created.

17/9/18 Steph
* Brief meeting with course convenor with project update
* Emailed client about project updates and forwarded correspondence from ethics committee
* Emailed other course lecturer about medical devices
* Made agenda for tutorial tomorrow 18/9
* Begun agenda for group meeting 19/9
* Written up audit 2 feedback summary, lawyer meeting summary and human ethics committee summary of correspondence

24/9/18
* Brief meeting with course convenor on biomedical materials  to discuss purpose of the device
* No new information for project

25/9/18 Joey
* Reworked sections of the ConOps (as seen in change log in rebranding patch).

26/9/18 Joey
* Began changes to requirements document with rebranding.

29/9/18 Joey
* Completed changes to requirements and testing documents.

1/10/18 Joey
* ConOps v1.1 pdf created based on version in patch.

8/10/18 Steph
* Client feedback document created in resources
* Conops v1.1 updates as per client feedback (see change log)
* Created Audit 3 presentation and poster survey
* First draft of Handover document
* Microgrant 2.0

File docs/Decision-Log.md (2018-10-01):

# Decision Making Strategy
In order to make decisions that will have a significant effect on the project the team must come to a consensus decision. The following steps will be taken to strive for independent thought preceding each decision and ensure acceptance of the final decision:

1. Each member of the project team will be given the opportunity to state their perspective uninterrupted by the rest of the team.
2. If perspectives differ then a collaboration or compromise will be created so that the best possible decision can be made.
3. If the differences are not resolvable within the team then a majority 3-1 vote may be accepted to go accept a particular decision.
4. If the vote is split then the team will seek advice from stakeholders:
   * If the decision is design related the client will be contacted to have a final say on the decision.
   * If the decision is governance related then the shadow team will be contacted to provide insight and if necessary more votes (of which a majority of at least 7/10 will be accepted).
     * If an acceptable majority cannot be reached even with the shadow team then the tutor will be contacted for advice.
5. If after step 4 a decision still cannot be reached then the course convenor will be contacted as a last resort.

# Decision Log

| Date: | Stakeholders Involved | Decision Made: | Reason For Decision: | Effect on Project: |
| :---: | :---: | :---: | :---: | :---: |
| 2018-08-08  | Project Team  | Conduct research into medical device regulation and open source medical device projects | The team is aware that there are significant regulations surrounding medical devices by the branch of the government that regulates medical devices - The Therapeutic Goods Administration (TGA). The team needs to be sure that this device is not doing anything against current regulations and so research into medical devices should be conducted.  | First the research lead will work on determining how the TGA defines what a medical device is, to determine if this project falls under those regulations. From this, if necessary, the team will work on ensuring that we are complying with regulations - e.g. that we are not a manufacturer. This will lead into how open source devices are regulated and what processes other open source projects may have followed to remove liability if necessary.  |
| 2018-08-11 | Project Team | Commence New Development of Software | The HackADay code was not working as intended. The Networking segments of code where not applying, and as such we were not able to get a remote stream on a separate device. | Minimal. While some features could not be observed, it felt appropriate to move on and develop a more robust code to work with the device provided to us. The unobserved features (Brightness and Contrast controls) may still need to be considered, as they still affect the final product, and may slow development while the workings of these features be determined. |
| 2018-08-16 | Project Team | Manual Software Controls over Hardware Processing | Parameter editing required to be in place before they can be automatically adjusted | Will help understand how to create the automatic controls, as they should work by manual control firstly, before being handed over to software algorithms |
| 2018-08-18 | Project Team and Client | Utilise the power switches on the PiJuice, and implement a low power state. | Turning off the device may become a secondary concern for users as other processes may take precedence, such as properly disposing of any sharps used, or an urgent matter is raised with another patient. This leaves the device continually running to drain the battery, becoming unusable until it has been recharged. Implementing a power off/sleep timer will be of a benefit during a busy period in the workplace. | There is a concern that the streaming script will not continue should it resume for a low power state. testing will need to be done to see if this idea is viable. Alternatively, ensuring that the device boots from no power within 10-15 seconds is suitable. The auto off function should still be implemented to turn the device off if it is not already. |
| 2018-08-22 | Hardware Team | Order bulk 850nm IR LEDs | The 850nm wavelength has been seen to be near optimal for vein detection, as it is absorbed by the hemoglobin in our blood, and reflected by our skin to create the contrast we need to identify veins. Given this is important, a large batch was ordered for testing and final implementations. Other wavelengths will be purchased to compare against and possibly augment the 850nm LEDs. | Using these LEDs will hopefully give the best image contrast. however, testing a mix of higher and lower wavelengths may allow for better performance, as it may result in a deeper penetration of light. |
| 2018-08-23 | Software Team | Change of Streaming Method | Orignial streaming script was hard to modify as classes were confusing to interpret how they were setting up the bit streams. After hours of attempting to modify this code, it was eventually scrapped all together. Instead, a Flask script was found which allowed for OpenCV functions to be parsed into a stream. Initially there was difficulty feeding the video input from the PiCam directly into the stream. The solution to this was to iteratively have the PiCam take an image, apply a histogram equalisation, and feed the image into the stream. This is performed every time an image is taken, which is dictated by the given framerate. | Positive: processed image is now successfully streaming to an external device.
| 2018-08-23 | Software Team | Change to Framerate | Framerate of camera shutter set to 60 frames-per-second rather than <32. Increasing the framerate gave for a much darker yet smoother stream, and allowed objects focused under IR light to illumate far greater than they did at the lower framerate. This is most likely due to the lens having less time to take in external interfering light sources between each shutter. As a result, veins appear are far more clearly visible at the higher framerate. | Positive: knowing that the framerate directly correlates with the quality of the image allows for more thorough investigation into the best framerate for the clearest image. |
| 2018-08-24 | Hardware Team | Optimise Case Design | The case printed successfully, however some issues were immediately apparent. The case itself was too big to hold comfortably, which does not align with the project requirements, as well as the simple mounting solution for the Pi was not ideal and easily came away from the case. The LED array does not have a mounting solution as of yet. V1.1 addresses the mounting solution for the Pi, as well as some little issues that could be addressed immediately. v2.0 has started to address the size issue, and potentially the LED mounting solution | Positive. This is an iterative process that has started early and allows us to bring any physical issues to light, allows us to rectify them, and optimise the solution. |
| 2018-09-15  | Project Team  | Not to undergo testing  | Discussion with legal services brought up possible need for ethics approval for testing. This was then confirmed through email correspondence with the ANU Human ethics committee, expressly stating ethics approval would be needed for testing on humans for the project. This correspondence is comprehensively summarised in the Resources folder of the repository.  | As human ethics approval is an extended process, there is no time for this to be persued at this stage of the project, and the client would prefer if we did not spend resources persuing further information on this. Hence, testing outside of the project team is outside the scope of this project, and the project team accepts that this will limit improvements to the functionality of the device. Testing documents will be prepared for the future of the project but all other use of the device will be considered demonstration only and no notes or human aspects will be documented.  |
| 2018-09-19 | Software Team | Software Focus | Decision was unanamously made by team to have the primary focus for the software team for the remainder of the project to be the Flask/JS web interface to allow for manual variable control. This will include sliders and buttons to allow for the manual adjustment of camera attributes (saturation, brightness, contrast, etc) and the level of equilization/processing occuring to image. This decision was made in line with the decision to focus on the VeinCam to be an educational tool, and the manual control will allow users to have more control to see what variables will get the clearest vein images. | Positive: there is now a set goal and direction to be taken throughout the final weeks of the project. This decision will ensure "feature creep" doesn't greatly influence or affect the outcomes of the project. |
| 2018-09-22  | Project team and Client | Shift purpose of device to educational  | Through conversations with the therapeutic goods administration who regulate medical devices, the team became aware that by purposing the device as a medical device, they would not be able to distribute any information about how to make the device. With input from the client on what he is comfortable with going forward, the decision was made to move the focus from medical to educational purposes only.  | Hence changes were made to the Concept of operations and requirements as the device is no longer purposed for use in intravenous procedures, and the user of the device has now been changed. |
| 2018-09-22  | Project team and Client | Add cardboard template of case as alternative to 3D printing  | Was highlighted multiple times by the shadow team and tutor that 3D printing was not an accessible option for an open source project. Upon discussion within the team and with consideration from the client it was unanimously agreed the a simple but accessible alternative will be a cardboard net template that can be provided alongside the CAD designs for the case.  | Hardware team now needs to design this template so that a test print and construction of a basic cardboard case can be tested |
| 2018-09-29 | Project Team and Client | Rebuild System due to failures | During the meeting with the client, the device failed to both broadcast the WiFi consistently, and when it was able to be connected to, the web page failed to load. It was decided that the project team will maintain ownership of the device, and strive to get the device working as intended. The Hardware team decided to recover the code from the device, and rebuild the operating system, as it was believed that there may have been remnant software left over from previous testing. The device is to be handed back to the client 2/9/2018 so they have ample time to test the device. | Positive. Despite being a large set back, we know our final solution and can optimise the system for this solution exclusively. This has the potential to help performance of the device overall, as it will only have what is required. |
| 2018-10-01 | Hardware and Software | Maintain system backups of the device as checkpoints | Due to the failure presented on 29/9/2018, it was decided to maintain system backups of the device for quick resets to a particular point, reducing the time to prepare the operating system after another failure. | Positive. This will also allow us to provide a system image to be made available for users of the device, so that they can use their device within a fraction of the time to prepare the device. |

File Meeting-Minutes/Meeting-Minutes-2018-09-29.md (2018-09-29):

# Meeting Minutes 29/9/18

| Attending: | Absent: |
| :---: | :---: |
| Joey McPhail | |
| Steph Pratt | |
| Chris Bodger | |
| Alex Ollman | |
| Ben Healey | |

## Agenda
1. Project Update
   * Hardware
   * Software

---

## 1. Project Update
* Hardware
  * Steps to operate:
    * Turn on
    * Connect to wifi (RasPi related name)
      * Password: ChangeMe
    * Site: 10.3.141.1:8000
  * Can still get images from different LED configurations.
* Software
  * Check for SD card corruption.
* Device had some unforeseen issues to be fixed ASAP to give to Ben for examination on Tuesday.

---

## Actionables
* Chris to:
  * Take images of different LED configurations.
* Steph to:
  * 
* Alex to:
  * 
* Joey to:
  * 
* All:
  * Have full case and working software ready for tuesday.

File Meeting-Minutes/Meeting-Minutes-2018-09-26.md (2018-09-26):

# Meeting Minutes 26/9/18

| Attending: | Absent: |
| :---: | :---: |
| Joey McPhail | |
| Steph Pratt | |
| Chris Bodger | |
| Alex Ollman | |

## Agenda
1. ConOps and requirements sign-off
2. LED Testing
3. Poster

---

## 1. Sign-offs
* ConOps
  * Chris and Alex to address hardware changes
  * Adjust stakeholder analysis (user/public section)
    * Make reference to changed stakeholders in requirments when updated.

---

## 2. LED Testing
* Found source on wavelength vs skin penetration.
  * Demonstrated 850nm was more optimal.
* Verified by brief in-house testing.
  * Remaining with only 850nm LEDs.

---

## 3. Poster
* Content Brainstorm:
  * Timeline of the project with major decisions
    * Looks like a vein with branches to speech boxes.
    * Subsection of case development.
  * Aim of the project.
    * What it does.
  * How it works.
    * Image of the open case with how the hardware works.
    * How the image processing works.
  * More diagrams than words.
    * Image of the whole case.

---

## Actionables
* Chris to:
  * 
* Steph to:
  * Update stakeholder analysis in Rebranding-Patch.
* Alex to:
  * 
* Joey to:
  * Draft landscape and portrait poster mock-ups.
  * Update public landing page.
* All:
  *

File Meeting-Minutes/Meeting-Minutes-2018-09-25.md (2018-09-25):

# Meeting Minutes 25/9/18

| Attending: | Absent: |
| :---: | :---: |
| Joey McPhail | |
| Steph Pratt | |
| Chris Bodger | |
| Alex Ollman | |
| Jenny Simmons | |
| Shadow Team | |

## Agenda
1. Hardware
   * Alternative construction methods.
2. Software
3. Rebranding

---

## 1. Hardware
* 3 of each might not be getting enough light.
* Printing shell first.
* Alternative construction methods.
  * Could buy something and drill holes for cases.
  * 3D printing different sections could reduce error and fit them together after print.
  * As an education tool it will need less requirements. Dont need to be as specific with construction methods.

---

## 2. Software
* No additional feedback.

---

## 3. Rebranding
* Informed consent
  * Can also be used to give people an understanding of similar devices.

---

## Additional Feedback
* Poster draft needs to be ready for week 10 audit for marking/feedback.
* Need to start thinking about justification document (2-5 pages) applying for a grade.
* Complete how-to guide before audit to get feedback.

---

## Actionables
* Chris to:
  * 
* Steph to:
  * 
* Alex to:
  * 
* Joey to:
  * 
* All:
  *

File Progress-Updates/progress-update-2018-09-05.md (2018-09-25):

## September 5th
Progress this week has been based around finalising the prototype. This has taken longer than anticipated due to a few setbacks with 3D printing and finalising code.

### Hardware
Version 2.0 of the chassis has proved difficult to complete as there has been complications with the 3D printers. A version was printed however the mounting pins inside the case were malformed. An ad hoc mechanism may be used with the print and if the issue persists then an alternative will be chosen. Version 2.1 will be printed tomorrow with the hope that it will be suitable to hand to the client for preliminary testing.

### Software
A successful stream has been created with the automatic contrast adjustment. The next step is to get the Pi to run the necessary scripts on boot so that the process can be simple and automated when users turn on the device.

The goal is to complete a working prototype in both hardware and software to give to the client this Saturday (8th of September)

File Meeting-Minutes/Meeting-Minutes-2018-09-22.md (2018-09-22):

# Meeting Minutes 22/9/18

| Attending: | Absent: |
| :---: | :---: |
| Joey McPhail | Chris Bodger |
| Steph Pratt | |
| Alex Ollman | |
| Ben Healey | |

## Agenda
1. Project Update
   * Hardware
   * Software
2. Rebranding

---

## 1. Project Update
* Hardware
  * Testing the LEDs to check the brightness before printing again.
  * Could cut losses and attempt something like a laser cut box (or something else).
  * Prioritising getting something to Ben next week for him to provide feedback.
* Software
  * Prioritise manual controls
     * Whether that be sliders or option selection.

---

## 2. Rebranding
* Ben happy with the educational route.
  * State that it has not been approved for medical use.
  * Lets the project remain open-source.
* Alternatively say it's for something else but we've looked at it for educational purposes.
  * Renaming it is also an option.

---

## Additional Feedback
* Device hardware/software and use instructions should have higher priority than other documentation.

---

## Actionables
* Chris to:
  * LED testing leading to a final case design and last print attempt.
* Steph to:
  * 
* Alex to:
  * Add frame rate discoveries to decision log.
* Joey to:
  * 
* All:
  * Have something to give Ben next week, in either a new case or old case.

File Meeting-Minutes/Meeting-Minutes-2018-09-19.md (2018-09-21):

# Meeting Minutes 19/9/18

| Attending: | Absent: |
| :---: | :---: |
| Joey McPhail | |
| Steph Pratt | |
| Chris Bodger | |
| Alex Ollman | |

## Agenda
1. Audit feedback
   * Alternative printing and resin coating
   * Wireless charging
   * Need to update casing iterations into the decision log
   * Start using feedback forms in our internal testing and feedback from Ben
   * Document why certain things in the project are taking priority - need to add a summary of research decisions into decision log
   * Work on consulting external opinions regarding the hardware/software development
   * Rotating roles
   * Actionable and Issues on Github need to be kept up to date
   * Feedback from Jenny that there are some gaps in the repository that have been present for a while
   * More regular commits of software updates in the repository
   * Clearly state the goals of the project going forward - probably need to update feedback

---

## 1. Audit Feedback
* Resin coating optional extra. Not a priority.
* Magnets could interfere with wireless charging. Future development.
* Actionables to be added to issues after meetings.
* Goals:
  * Prioritise manual adjustment
  * Checking different wavelength LEDs
  * Will be updated with new ConOps
  * Tutorial and user-feedback form for testing when ethics is approved

---

## Hardware Update
* Might integrate 12 LEDs instead of 6.
  * If 3 LEDs has good results.

---

## Software Update
* Manual Adjustment or Image Processing?
  * Prioritise manual adjustments.
    * Hue, saturation, etc.
    * Changing the power levels of different wavelength LEDs.

---

## TGA Feedback
* We are considered the manufacturer (aligning with EU law)
* If we reframe the device and repurpose it as just an IR camera then we wouldn't be manufacturers as it wouldn't be a medical device.

---

## For Client Meeting
* Examine rebranding options (educational or other).

---

## Actionables
* Chris to:
  * Update 3D printing design changes between versions.
* Steph to:
  * Update decision log with research decisions.
* Alex to:
  * Update decision log with software decisions.
  * Upload poster template to Drive.
* Joey to:
  * Put actionables into Issues at the end of meetings.
* All:
  * Draft changes to ConOps and Website in terms of scope.

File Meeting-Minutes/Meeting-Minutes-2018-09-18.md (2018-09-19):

# Meeting Minutes - 18/9/2018

| Attending: | Absent: |
| :---: | :---: |
| Joey McPhail | |
| Steph Pratt | |
| Chris Bodger | |
| Alex Ollman | |
| Jenny Simmons | |
| Shadow Team | |

## Agenda
1. Governance/Bureaucratic Issues
   * Medical device classification and manufacturer issues - see documents in Resources file 'Medical Device Classification' and 'Medical device manufacturer'
   * Meeting with ANUSA Lawyer - summary of outcomes in Resources 'Lawyer Meeting Summmary'
     * The safest definition is that we are a manufacturer and it is a medical device
     * Need to re-think the main outputs of the project
     * Human ethics approval needed for testing
   * Emailed Therapeutic Goods Administrations about open source project regulations
   * Emailed a course lecturer about medical devices
   * Correspondence with ANU Human ethics committee - summary in Resources 'Human Ethics Committee Correspondence'
     * Need approval before any testing done
     * Will get the ball rolling on this
   * Meeting with Technology Transfer office Tuesday 18/9 in afternoon
     * Aim to get a second opinion about medical devices, manufacturer definitions and open source projects
     * Get a brief idea of how we could get startup funding
     * Any other advice on how to go forward with getting the device out there in the future
   * Overall changes
     * Not going to make the device open source - not going to provide a how-to tutorial
     * Going to work on restructuring repository and review purpose and main goals of the project
     * Purpose now to product a functional prototype
     * Will still do testing, but only on ourselves and Ben
   * Can use the device for demonstrations, without formal data
   * Client does not want to waste time pursuing commercialisation
2. Hardware/Software Developments
   * Hardware
     * V2.1 of case failed to print several times
       * Required to order new filament
       * Printing will recommence today under full supervision
     * Testing of LEDs will commence
       * Determining an optimal mix of different wavelengths for deeper penetration
       * Final mix will be implemented into the final design
   * Software
     * Decision to discuss: what's first to complete? Manual Control or Image Enhancement
     * Focus will be placed on perfecting selected feature and attempt other as a reach goal.
     * Next primary goal will be to communicate with external LEDs to indicate status of device.
     * Automatic Script Startup and HTML processed image streaming now functional.

3. Feedback
   * Feedback summary now up from Audit 2 - Resources file. Full actions and justifications where necessary - feedback from that?
   * Some things no longer relevant since re-structuring the goals of the project - testing recommendations, etc
   * Starting to look into alternative methods of construction of case
   * Many comments about updating decision log; ensure decisions are well documented
   * Been seeking external opinions about a lot of these regulatory issues - aim to seek other opinions about hardware/software
   * Some comments about the distribution of jobs not being even and the distribution of and the distribution of administrative roles
   * Rotating roles
   * Progress update explicitly state how the project is progressing against each milestone - this is a good idea coming up to the end of the project and with the shift in the project goals

---

## 1. Governance/Bureaucratic Issues
* Testing on different body parts for alternate BMI.

---

## 2. Hardware/Software Developments
* Magnets used to hold device to stand.
* Will address outcomes in the next meeting.

---

## 3. Feedback
* Nothing to add.

---

## Additional Feedback
* Think about how to demonstrate the exemplary levels of assessment criteria.

---

## Actionables
* Chris to:
  *
* Steph to:
  *
* Alex to:
  *
* Joey to:
  *
* All:
  *

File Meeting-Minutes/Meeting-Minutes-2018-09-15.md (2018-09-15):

# Meeting Minutes - 15/9/2018

| Attending: | Absent: |
| :---: | :---: |
| Joey McPhail | |
| Steph Pratt (called in) | |
| Chris Bodger | |
| Alex Ollman | |
| Ben Healey | |

---

## Agenda
1. Project Update.
   * Waiting on more PLA.
   * Stream working, implementing java.
   * Preliminary testing documents
2. Concerns about some bureaucratic aspects of the project.

---

## 1. Project Update
* Works on boot.
* Using different wavelength of LEDs to overcome difficult use cases.
  * Implementing different LEDs and change intensity to optimise for different use cases.

---

## 2. Bureaucracy
* Would be classified as a medical device, where we are the manufacturers and responsibilities then lie there.
* Testing on patients in a hospital is out of the question.
* Can take the perspective of continuing the project through another semester and preparing things for another group.
* Moving the repository to a private one and not releasing any more information publicly.
  * At the moment nothing there is not already publicly available.

---

## Additional Feedback
* Assume we have the limits and continue with the device development.
* Rescope to aim for handover in week 10.
  * Documentation to support that.

---

## Actionables
* Chris to:
  * Purchase LEDs
* Steph to:
  * Organise meeting with Chris Browne.
  * When google drive ask Chris to change repository link.
* Alex to:
  * 
* Joey to:
  * Reorganise Google Drive and GitHub so the Drive is the main repository.
* All:
  * Meeting with Chris to update on state of the project.
    * Roadmap and prioritise goals.
    * Update Ben on outcomes.
  * Discuss poster.

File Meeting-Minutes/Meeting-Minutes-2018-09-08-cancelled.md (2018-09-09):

# Meeting Minutes - 8/9/2018
Meeting cancelled due to setbacks in 3D printing and team member commitments.

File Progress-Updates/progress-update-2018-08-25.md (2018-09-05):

## August 25th

### Hardware/Software

We have had a productive week on the hardware and software side of the project. We have successfully printed a prototype of the chassis, and have begun iterating on it to make it more suitable for the final product. A second print with some minor adjustments is underway and should be completed by our audit tutorial.

We found that the first chassis that was printed was quite large to hold, even by those with larger hands, and certainly would pose a challenge to hold by people with smaller hands. We determined that there was a lot of wasted space inside where the device is stored, and the next version will remove a lot of this space to slim down the device. The second version is currently being drawn up which will correct the dimensions and include a proper mounting system for the LED array, and after we have a time to inspect the v1.1 changes, more will be discovered and corrected in v2.0 and beyond. A new LED array will be constructed to be embedded in the new chassis.

On the side of software, we were able to achieve a histogram equalisation of a single frames, and push those frames to a local high frame-per-second video stream. This is a huge step towards our next milestone, and a step closer to finalising our product. The next goal for the project software is to feed the equalized video stream into the web stream so it can displayed on an external device, as well as applying colour filtering to further enhance the definition of veins.

### ANU Open Day

The VeinCam team volunteered to showcase the project to visitors, including many ANU student prospects, during this year's ANU Open Day. Throughout the day, we aimed to try and gauge public interest and acceptance, as well as user testing and receiving specific feedback. It was great opportunity to have a large number of people of diverse skin types test our product to determine where we can improve the product at such an early stage so we can gauge what adjustments need to be made.

We tested the device on many different skin colours, and noticed the skin tone appeared to not be an issue in displaying a prominent image of the veins, with both lighter skin tones and a range of darker skin tones tested.  A substantial amount of arm hair was thought to be an issue with vein detection, but this was proved not to be the case, as the small sample of testers with a significant portion of arm hair had their veins show up quite clearly.

We had a small number of people with skin conditions visit, including eczema, calloused skin and blemishes. Unfortunately, the device was not able to detect veins underneath sections where calloused skin was present, which we thought it due to the areas being to thick for the IR light to penetrate. The other skin conditions were no issue in regards to vein detection. There were no tests on those with tattoos on the day.

Vein detection through varying degrees of body fat was a primary concern of our client. Some testers came through with larger amounts of body fat around their arms, or simply had veins that were not on the surface of the skin, in which they were not able to have their veins detected by the device. The ability to detect veins through varying degrees of tissue will be very important function to focus on, as it may potentially determine whether or not our product can be used by a majority population and thus meet our project goals.

It was also observed that lots of external lighting, most prominently fluorescent lights and sunlight, produce enough infrared (IR) light to affect our project's ability to clearly deifne veins. The histogram equalisation software was not able to adjust the contrast of the stream as there was too much ambient IR light in the room, and skewed the histogram of the image itself to be more in the whiter zones, and washing out the darker zones. We are still looking into ways of resolving this, but one method may be purchasing an IR filter for the device for a longer wavelength (~800nm) so more light is filtered out, and hopefully making the overall image darker. A software solution may exist which we will also be exploring.

Overall, our project received a lot of interest and patrons were intrigued and impressed with what we presented on the day; validating our progress and urging us to continue moving forward.

### Other Admin/Governance
Regarding documentation updates, we have now received signoff from all stakeholders for our Concept of Operations. Research is well underway to get a good idea of the product market, as well as information on commercialisation and medical procedures around the VeinCam.

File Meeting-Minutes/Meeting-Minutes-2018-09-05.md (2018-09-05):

# Meeting Minutes - 5/9/2018

| Attending: | Absent: |
| :---: | :---: |
| Joey McPhail | |
| Steph Pratt | |
| Chris Bodger | |
| Alex Ollman (called in) | |

---

## Agenda
1. Progress update

---

## 1. Progress Update
* v2.0 of the print has some issues:
  * Mounting pins did not print well.
  * The lid is ok, so might just have to reprint the base and re-examine mounting mechanism for internal hardware.
  * Having issues with the printers themselves.
* Stream is working from a desktop and streaming well.
  * Web-page takes a while to load and does not work on different machines (or browser etc.)
  * Trying to get it to start on boot.
    * At the moment it is booting as root user, not pi user and does not like loading aspects of the software.
* Website development
  * Basic site architecture created.
  * Site pages started.

---

## Actionables
* Chris to:
  * Readjust v2.0 of the chassis and upload revisions and buttons.
* Steph to:
  * 
* Alex to:
  * 
* Joey to:
  * Format documents (research summary) in the repository.
  * Create a project update
* All:
  *

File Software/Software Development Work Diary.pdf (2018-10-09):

# Software Development Work Diary

Alexander Ollman
Software Team Lead
VeinCam ENGN4221 Project - 2018

## Week 3

Loaded Raspbian image onto provided Raspberry Pi. Installed required packages, including OpenCV which was used by the Venenfinder project.

The Venenfinder HackADay code was not working as intended. The networking segments of code where not applying, and as such we were not able to get a remote stream on a separate device. However, this code, supported by the Picamear documentation, gave us a great introduction to initializing the Raspberry Pi camera and taking photos/images with its library functions.

References:
https://github.com/Myrijam/Venenfinderhttps://hackaday.io/project/26158/logs?sort=oldesthttps://picamera.readthedocs.io/en/release-1.13/recipes1.html

## Week 4

Script found to stream video to bit stream, which could then be fed into HTML server.

References:
https://randomnerdtutorials.com/video-streaming-with-raspberry-pi-camera/

## Week 5

Began exploring image processing techniques to make veins clearer, more apparent and stand out from the rest of the image. The first technique trialled was performing a histogram equalisation on the image, which normalizes the contrast over the image. As a result, with veins absorbing the most infrared light, the veins were very dark and visible in comparison to the rest of the image. This processing was performed using code similar to the OpenCV tutorial on histogram equalisation. The processing occurred in what appeared to be real time.

For the ANU Open Day, two video streams (one with image processing, one without) was setup locally on the RasPi and displayed via a connected external monitor. There appeared to be no issues with the processing or the stream.

Needed to find some way to apply the histogram equalisation to the video web stream. As incoming frames were being fed directly into the web stream, many hours were spent attempting to “intercept” this video stream to perform image processing. This proved to be unsuccessful, as the web video streaming script used functions that were quite hard to understand their internal workings with my limited knowledge of Python.

References:
https://hackaday.io/project/13329-yet-another-ir-vein-detector
https://opencv-pythontutroals.readthedocs.io/en/latest/py_tutorials/py_imgproc/py_histograms/py_histogram_equalization/py_histogram_equalization.html (https://opencv-python-tutroals.readthedocs.io/en/latest/py_tutorials/py_imgproc/py_histograms/py_histogram_equalization/py_histogram_equalization.html)

## Week 6

Original streaming script was hard to modify, as classes from script found online were confusing to interpret how they were setting up the bit streams. After hours of attempting to modify this code, it was eventually scrapped all together. Instead, a Flask script was found which allowed for OpenCV functions to be parsed into a web stream. Initially, there was difficulty feeding a continuous video input from the PiCam directly into the stream. The solution to this was to iteratively have the PiCam take the last captured frame from the video stream and save it locally as a jpeg image, apply a histogram equalisation, and then feed that saved image back into the stream. This is performed every time an image is taken, which is dictated by the given framerate.

A video framerate of set to 60 frames-per-second was chosen rather than the previously used 32. Increasing the framerate gave for a much darker yet smoother stream, and allowed objects focused under IR light to illumine far greater than they did at the lower framerate. This is most likely due to the lens having less exposure time, thus taking in less external interfering light sources between each shutter. As a result, veins appear are far more clearly visible at the higher framerate under infrared light.

References:
https://blog.miguelgrinberg.com/post/video-streaming-withflask (https://blog.miguelgrinberg.com/post/video-streaming-with-flask)

## Week 7

Decision was made unanimously by the team to have the primary focus for software development for the remainder of the project to be the Flask/JS web interface to allow for manual variable control. This will include sliders and/or buttons to allow for the manual adjustment of camera attributes (saturation, brightness, contrast, etc) and the level of equalization/processing occurring to image. This decision was made in line with the decision to focus on the VeinCam to be an educational tool, and the manual control will allow users to have more control to see what variables will get the clearest vein images.

Began into finding articles relating to sending variables (such as slider values) from HTML to Python via Flask. This required learning a lot about how a Flask server works in a very short period of time, most of which was through trial and error. Found a script that allowed for a variable to be sent and saved in Python upon pressing a button. Most attempts were not successful as each Flask “route” (function) a HTML form could trigger would take the webpage away from the main page. Could not find a way to refresh page and/or redirect to the main webpage upon clicking aforementioned button.

References:
https://stackoverflow.com/questions/43677564/passing-input-from-html-to-python-and-backhttps://stackoverflow.com/questions/29884654/button-that-refresh-page-on-click

## Week 8

Discovered all that was required was to have each buttontriggered function return the index() function after saving the parsed variable, which would then reload the main web page. Variables could now be sent/functions could now be triggered from a HTML page to a Python script.

## Week 9

Attempted many trial-and-error methods of modifying the camera_opencv and base_camera scripts to be able to take in the saved Python variables from app.py as an imported library. This did not work. Figured instead to save variables locally to a text file that could be read and written by all scripts involved.

Parameter sliders were designed in two parts. The first part was to have the value of a HTML slider (0 – 100) be saved to a text file. The second part was adjusting the camera_opencv.py script to read the value in the text file and set the camera’s associated parameter to that value. Using W3School’s slider tutorial and Flask application instructions, able to take current slider value and save to text file. Learned how to read and write text files in Python.

Used same read/write functions to read a text file and use value as camera parameter (such as camera.brightness). After a few tests, it was determined that it was best to have these text files be read during the image processing of every frame, so that the parameters would be updated for the following frame. This would incur a visible update delay of 1 second to the stream, but we figured this was still suitable for purpose.

References:

https://www.w3schools.com/howto/howto_js_rangeslider.asphttps://stackoverflow.com/questions/6648493/open-file-for-both-reading-and-writinghttps://picamera.readthedocs.io/en/release-1.10/api_camera.html

## Week 10

Made the decision with client to move away from sliders to adjust parameters of camera and use large buttons instead, so that all devices can easily use.

Buttons adjust +-10 of each parameter.

Attempted to see if variables updating camera parameters could happen dynamically, or without requirements to refresh page. Discovered this will most likely require JavaScript. Given time constraints, this was figured to be left as a future improvement should the project be continued.

Webpage HTML updated to final design, including colour scheme and button styling. Used imported PiJuice functions to gather status of battery. These functions returned as python dictionaries, of which I was unfamiliar with. Found functions to extract values for charging status and battery charge percentage, which were then used in app.py to parse to the web page. This allowed users to know the battery percentage of the system at any time, and know if the device was charging properly when connected to power (seeing as, at this point of hardware development, there were no visible battery indicator lights outside of the enclosure).

Feedback from Ben was to have stream portrait as opposed to landscape, as most devices will be portrait orientated and thus can better view a persons arm. Rotating image using camera.rotation object parameter or in HTML/CSS did not properly rotate the image, or scale properly for multiple device browsers. Found OpenCV script by Adrian Rosebrock which performed perfect matrix rotation of image array without cropping or resizing image. Parsing the rotated image straight to webpage presented no issues with resizing.

Attempted to localise font within CSS so that all devices can view desired ‘Baloo’ font. Was not successful as this is not a default HTML5 font and with the device streaming over a local WLAN, connected devices will not have internet access to import the font. Instead, we will opt for similar but compatible font to use during poster presentation.

References:
https://github.com/PiSupply/PiJuice/tree/master/Softwarehttps://www.w3schools.com/css/css3_buttons.asphttps://www.pythonforbeginners.com/dictionary/how-to-use-dictionaries-in-python/https://www.pyimagesearch.com/2017/01/02/rotate-images-correctly-with-opencv-and-python/

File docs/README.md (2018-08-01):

# VeinCam Landing Page

## Table Of Contents
1. [Progress Update](#1-progress-update)
2. [Audit Log](#2-audit-log)
3. [Concept of Operations](#3-concept-of-operations)
4. [Meeting Minutes](#4-meeting-minutes)
5. [Design Documents](#5-design-documents)

## 1. Progress Update
Currently, we are preparing for Audit 1 by creating the project documentation. This includes:
* Project requirements
* Concept of Operations
* Stakeholder Landing Page
* Work Breakdown Structure and Gantt Chart
* Basic Structure of the Repository (this will evolve as the project proceeds)

We hope to have this all ready to present to our stakeholders during our tutorial, otherwise have it completed by the end of the audit period.

#### Previous Progress Updates
* Not applicable yet

## 2. Audit Log
Here we will have the information, results, and feedback to our audits, and will be presented in the following links (as they are created):

* Audit 1
* Audit 2
* Audit 3

Should our stakeholders wish to provide us with feedback, they can fill out a google survey in which we will action them appropriately as responses are presented to us.

## 3. Concept of Operations
Our Concept of Operations is still being drafted, and yet to be signed off. we hope to have this completed by the end of the audit period, in which we can continue with the project.

The [Concept of Operations](CONOPS.md) document can be found in our repository.

## 4. Meeting Minutes
Team meetings are scheduled twice a week, to ensure the team is aware of the overall progress made, as well to provide the client an opportunity to see what we have achieved, should they choose to join the meetings. They are currently scheduled for the following times:
* Wednesday 12pm
* Saturday 2pm

These times may vary, depending on the availability of the team, and client.

Meeting Minutes can be found in our repository.

## 5. Design Documents
The design of the VeinCam will be presented here, once the ConOps has been approved, and progress/final designs are made available. the construction method of the device will also be presented here.

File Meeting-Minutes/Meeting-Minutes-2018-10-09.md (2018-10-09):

# Meeting Minutes 9/10/18

| Attending: | Absent: |
| :---: | :---: |
| Joey McPhail | |
| Steph Pratt | |
| Chris Bodger | |
| Alex Ollman | |
| Chris Browne | |
| Shadow Team | |

## Agenda
1. Presentation
2. Feedback
3. Poster Feedback

---

## 1. Feedback
* ON/OFF labels.
* Sanding to smooth the surface.

---

## 2. Poster Feedback
* Collected in sheets
* Verbal:
  * Have comparison of images through (and not through) the VeinCam lens.
  * Images instead of text for scenario/problem/resolution.

---

## Actionables
* Chris to:
  * 
* Steph to:
  * 
* Alex to:
  * 
* Joey to:
  * 
* All:
  *

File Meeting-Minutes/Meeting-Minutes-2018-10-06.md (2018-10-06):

# Meeting Minutes 6/10/18

| Attending: | Absent: |
| :---: | :---: |
| Joey McPhail | |
| Steph Pratt | |
| Chris Bodger | |
| Alex Ollman | |
| Ben Healey | |

## Agenda
1. Future of the project.
   * Client feedback on manual control.
   * What the repository and website will look like.
2. Client Feedback (google drive)
   * Conops- some small changes
   * Device use

---

## 1. Future of the project
* UI
  * Remove slider, have an add or subtract button is ok (or have multiple settings).
* Repo
  * Leaving it as a Github repo is good for open source.
    * Shift ownership from Chris to Ben
  * Can use Ben's contact details on the repo, poster and public pages.

---

## Actionables
* Chris to:
  * 
* Steph to:
  * 
* Alex to:
  * 
* Joey to:
  * Update website.
* All:
  *

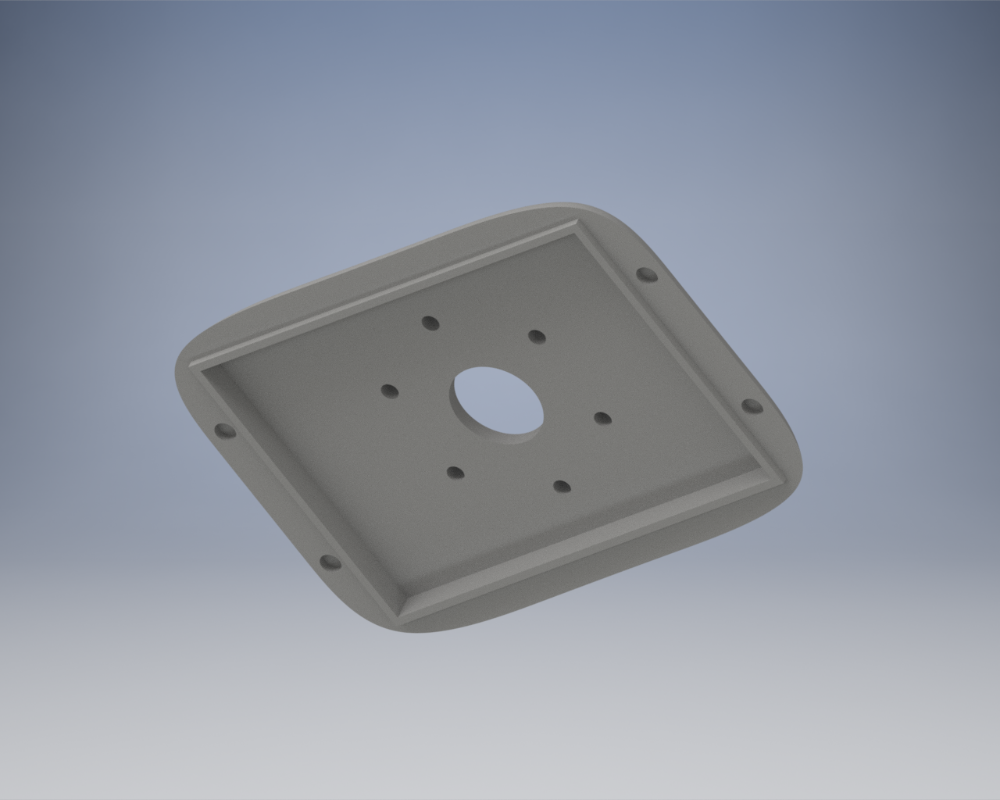
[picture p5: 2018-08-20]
images/design-images/lid-inside-1.png

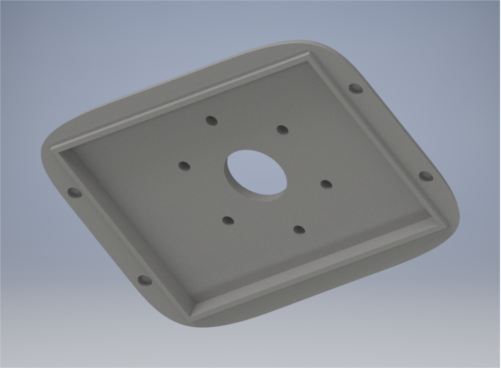
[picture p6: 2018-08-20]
images/design-images/lid-inside-1-crop.png

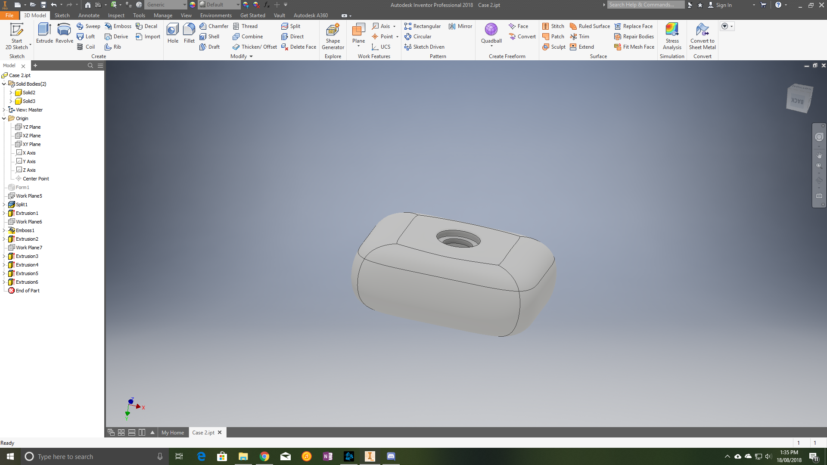
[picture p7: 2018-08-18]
images/design-images/overall-look.png

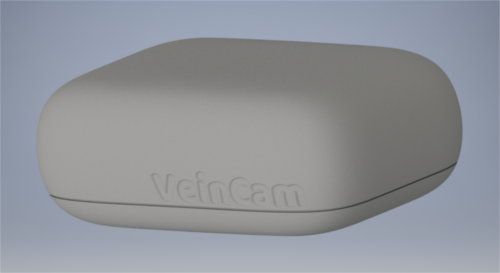
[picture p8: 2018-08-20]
images/design-images/side-render-1-crop.png

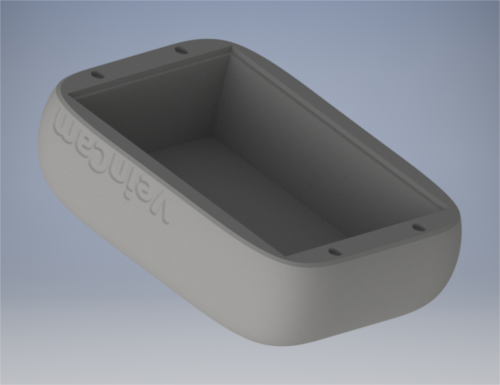
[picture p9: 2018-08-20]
images/design-images/inside-render-1-crop.png

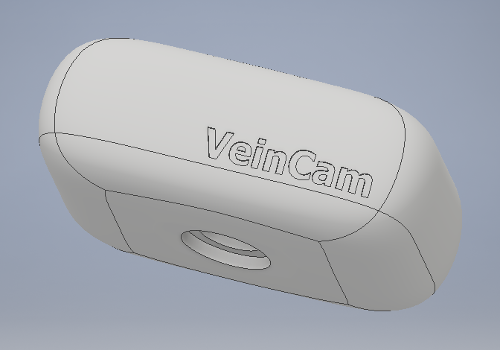
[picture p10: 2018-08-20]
images/design-images/shameless-branding-crop.png

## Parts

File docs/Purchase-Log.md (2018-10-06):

# Purchase Log

## Future Expenses
| Item Description | Available From | Cost  | Needed By | Microgrant Approved | Date Approved |
| :---: | :---: | :---: | :---: | :---: | :---: |
| | | | | | |

## Incurred Expenses
| Item Description | Obtained From |  Date Obtained  | Cost | Microgrant Approved | Date Approved | Reimbused?  |
| :---: | :---: | :---: | :---: | :---: | :---: | :---: |
| 5mm 850nm Infrared Transmitting LED, Quantity 25  | Little Bird Electronics Website: https://www.littlebirdelectronics.com.au/led-infrared-850nm-25-pack  | | Cost $12.29 for 25 pack, Postage $9.40, Total $21.69  | Yes | 27/8/18 | No  |
| 5mm 940nm Infrared Transmitting LED, Quantity 10  | Available at Jaycar electronics Website: https://www.jaycar.com.au/5mm-infrared-transmitting-led/p/ZD1945 | | Cost: $1.35 (for quantity 10-24), total $13.50  | Yes | 27/8/18 | No  |
| 1kg ESUN PLA+ Filament (White) | Kingdom3D Printing: https://www.kingdom3d.com.au/collections/3mm-filament/products/esun-3d-printer-filament-3mm-pro-pla-1kg?variant=30424627265 | 7/09/2018 | $24.90, $8.90 Postage, Total $33.80  | TBD | TBD | No |
| 5mm x 2mm Disk Magnets, Quantity 20 | SimplyOnline Ebay Store: https://www.ebay.com.au/itm/152688785592 | 27/08/2018 | $3.85 | TBD | TBD | No |
| 20mm x 10mm x 3mm Cuboid Magnets, Quantity 3 | SimplyOnline Ebay Store: https://www.ebay.com.au/itm/152689101658 | 17/09/2018 | $4.50 | TBD | TBD | No |
| 75mm x 95mm Prototyping Board | Available at Jaycar electronics Website: https://www.jaycar.com.au/pc-boards-vero-type-strip-95mm-x-75mm/p/HP9540 | Cost: $4.50 | | Yes | 27/8/18 |
| 5MP Camera Module for Raspberry Pi | Available at Jaycar electronics Website: https://www.jaycar.com.au/5mp-camera-for-raspberry-pi/p/XC9020 | Cost: $24.95 | | Yes | 5/10/18 |

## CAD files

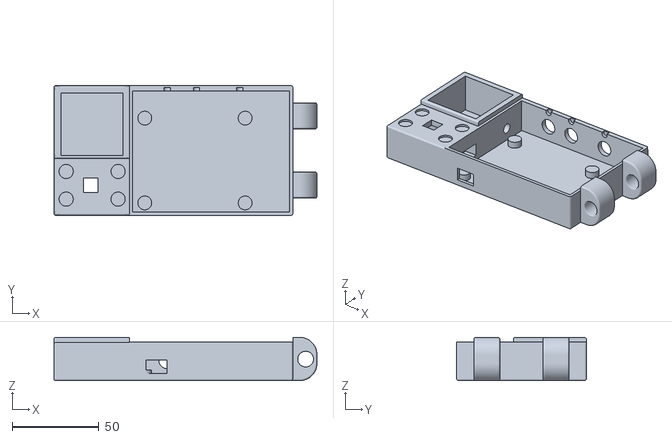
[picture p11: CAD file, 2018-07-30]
Resources/Venenfinder Resources/3d_files/Vene_main_case.stl
152.0 x 75.0 x 25.0

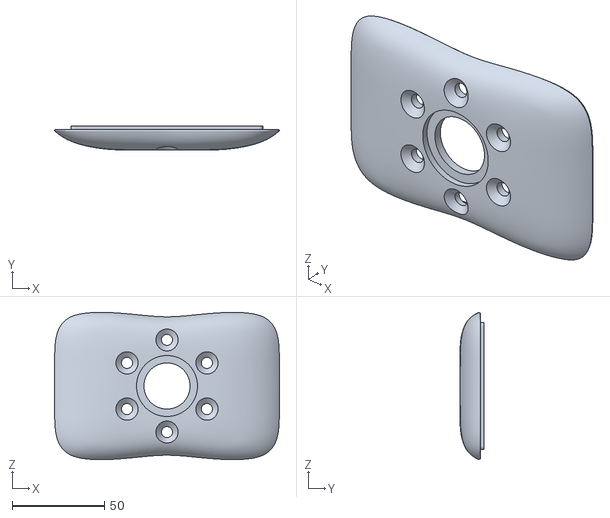
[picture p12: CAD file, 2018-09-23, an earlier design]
CAD-Drawings/v2.2/Casing-v2.2 Lid.stl
121.9 x 13.0 x 79.8

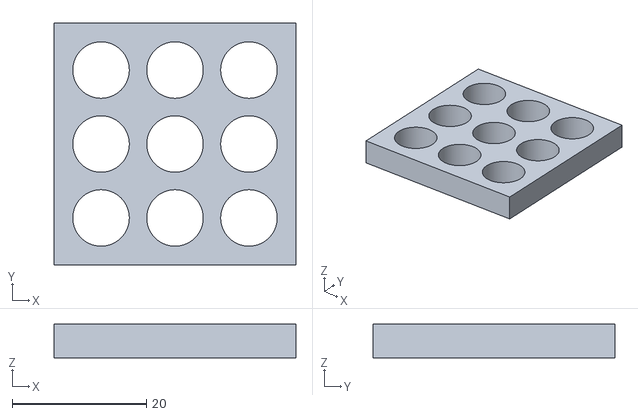
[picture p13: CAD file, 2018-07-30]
Resources/Venenfinder Resources/3d_files/IR-LED-reflector-Matrix_Venenfinder.stl
36.0 x 36.0 x 5.00

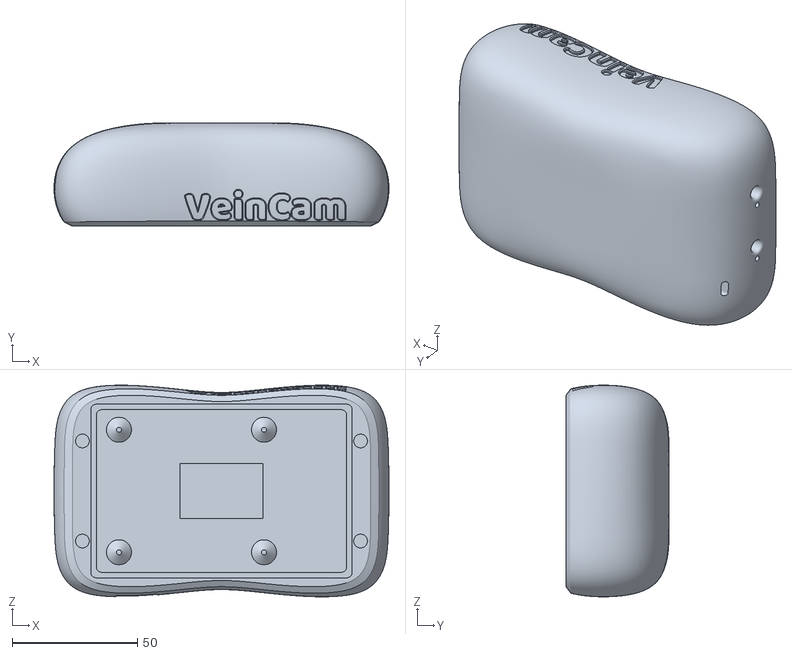
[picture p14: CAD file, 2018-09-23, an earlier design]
CAD-Drawings/v2.2/Casing-v2.2 Shell.stl
134.0 x 41.2 x 84.6

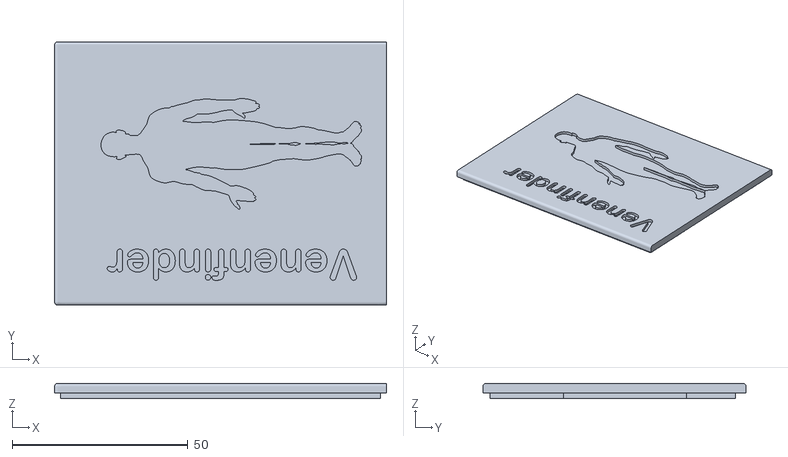
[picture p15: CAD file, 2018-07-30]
Resources/Venenfinder Resources/3d_files/Cover_Venenfinder.stl
94.5 x 75.0 x 4.40

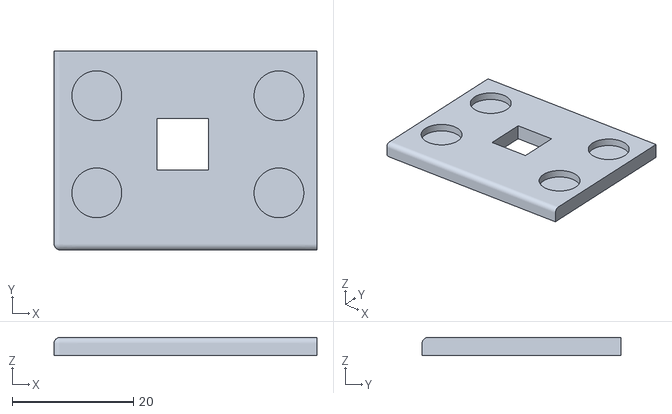
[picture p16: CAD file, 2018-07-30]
Resources/Venenfinder Resources/3d_files/IR-Filter_MagneticClip_Venenfinder.stl
43.3 x 32.8 x 3.00

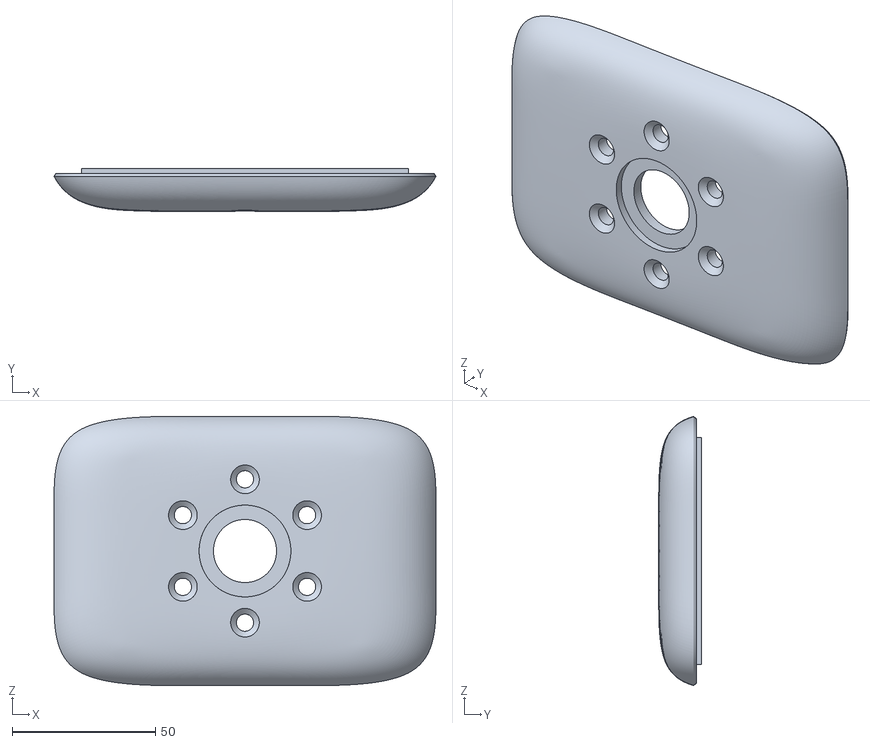
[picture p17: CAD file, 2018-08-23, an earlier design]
CAD-Drawings/v1.0/Casing-Lid-v1.0.stl
133.2 x 14.9 x 93.9

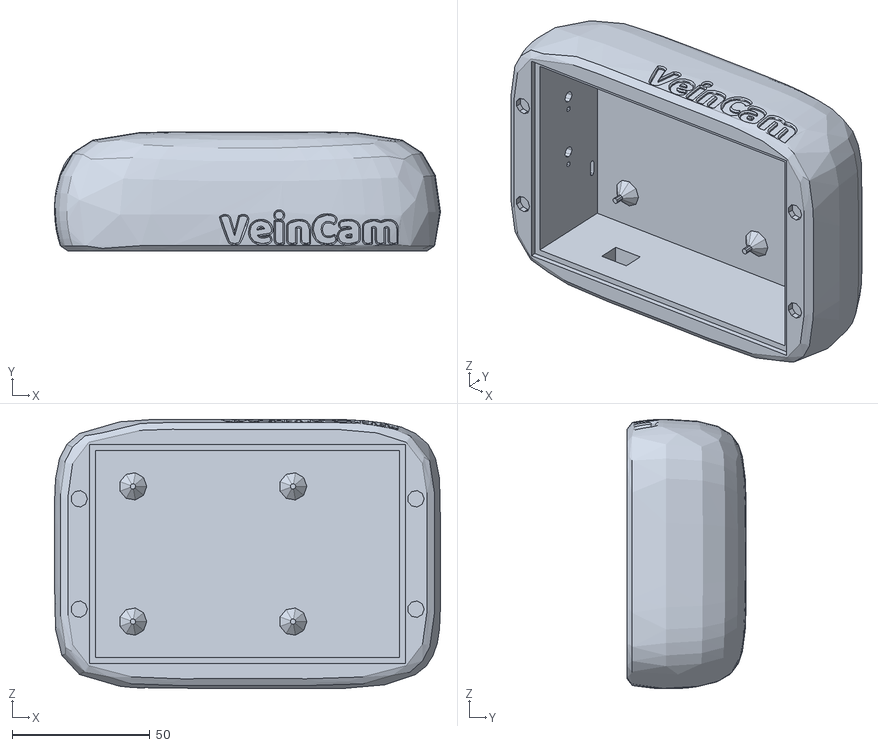
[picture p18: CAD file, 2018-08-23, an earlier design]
CAD-Drawings/v1.1/Casing-Shell-v1.1.stl
139.9 x 43.1 x 97.6

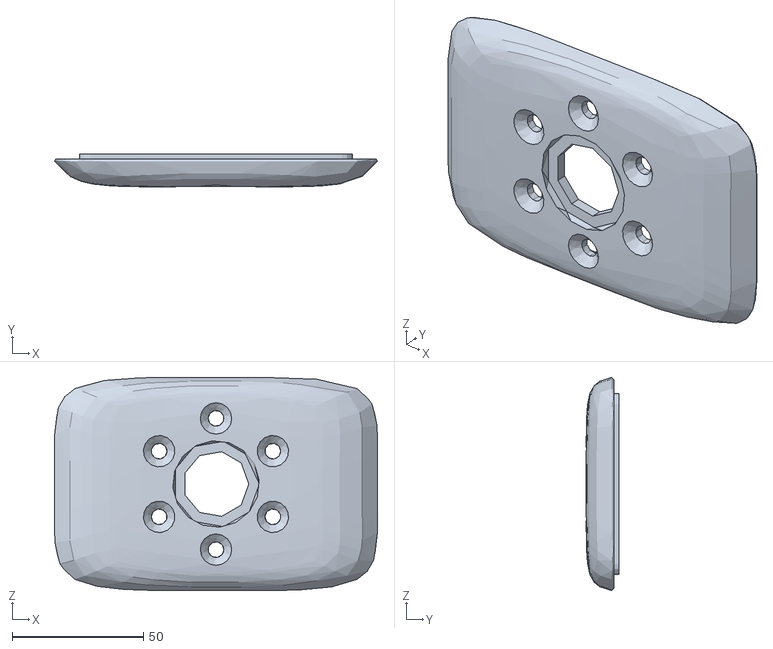
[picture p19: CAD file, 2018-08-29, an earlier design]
CAD-Drawings/v2.0/Casing-Lid-v2.0.stl
123.0 x 12.4 x 81.1

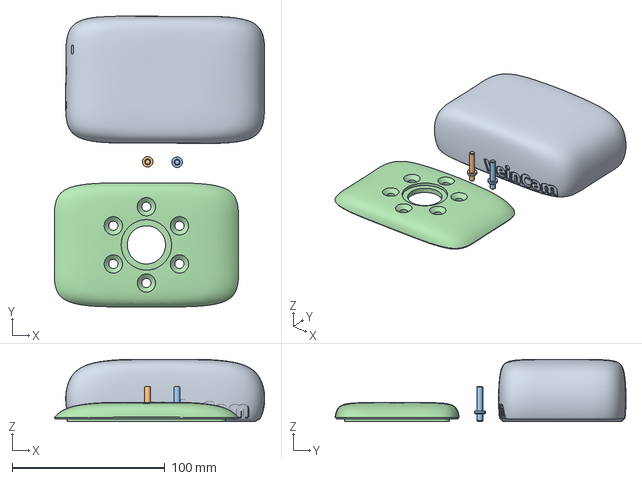
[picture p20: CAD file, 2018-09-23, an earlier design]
CAD-Drawings/v2.1/UM2_Casing-v2.1-shell-and-lid.3mf
137.9 x 190.6 x 40.6 mm

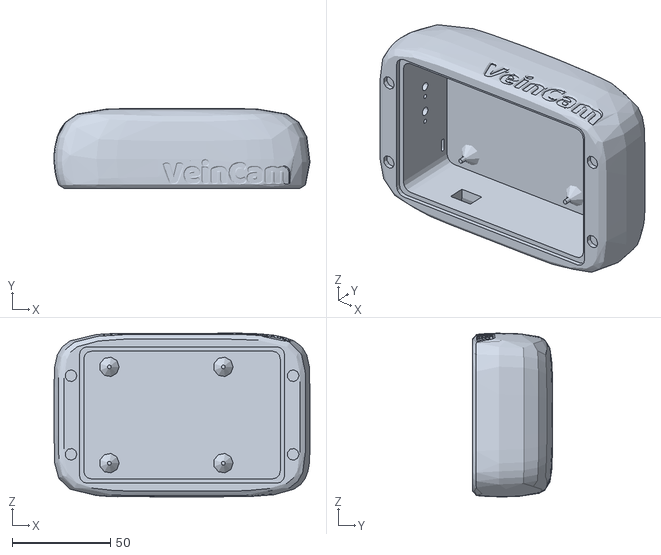
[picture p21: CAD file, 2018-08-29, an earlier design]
CAD-Drawings/v2.0/Casing-Shell-v2.0.stl
130.3 x 40.6 x 83.2

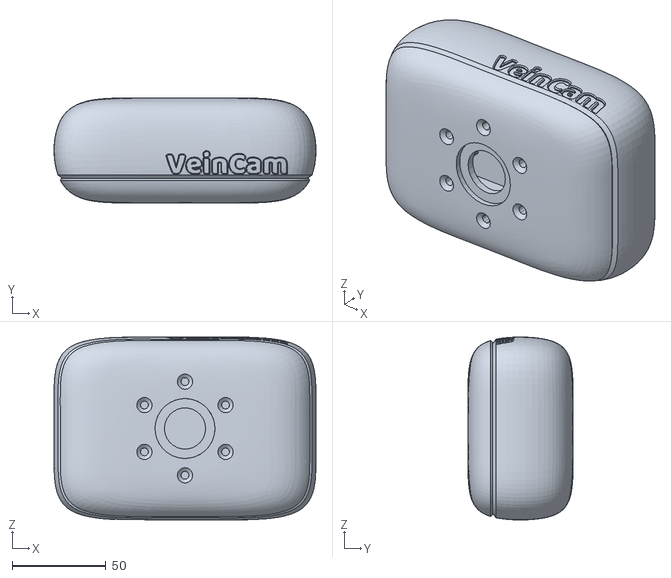
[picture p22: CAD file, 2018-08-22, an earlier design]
CAD-Drawings/v1.0/Casing-v1.0.stl
139.9 x 56.3 x 97.6

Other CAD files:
CAD-Drawings/v1.0/Casing-Shell-v1.0.stl
CAD-Drawings/v2.1/Casing-v2.1lid.stl
CAD-Drawings/v2.1/Casing-v2.1-shell.stl
CAD-Drawings/Casing.ipt
CAD-Drawings/v2.1/OldVersions/Casing-v2.1.0003.ipt
CAD-Drawings/v2.1/button.ipt
CAD-Drawings/v2.1/button.stl
CAD-Drawings/v2.3/button.ipt

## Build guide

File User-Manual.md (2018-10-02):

## Prototype Instructions (version b1.0)

To use the device and stream the camera image to your own personal device:

#### 1. Turn on device, press the right button (lid/LEDs facing upright).
#### 2. Wait 20 seconds for startup.
#### 3. On your personal device, go to the WiFi settings and select the 'VeinCam' network (Password: ANUVeinCam)
#### 4. Go the browser on your device
#### 5. Enter the address '10.3.141.1:8000' (no quotations).
#### 6. View the stream!

To switch off the device, press the left button (lid/LEDs facing up).

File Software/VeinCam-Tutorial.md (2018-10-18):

# Table of Contents
1. [Required Hardware](#required-hardware)
2. [Assembling the Raspberry Pi](#assembling-the-raspberry-pi)
3. [Assembling the LED Array (WARNING: BURN HAZARD)](#assembling-the-led-array-warning-burn-hazard)
4. [Preparing The Raspberry Pi for VeinCam (The Quick Way)](#preparing-the-raspberry-pi-for-veincam-the-quick-way)
5. [Preparing The Raspberry Pi for VeinCam (The Advanced Way)](#preparing-the-raspberry-pi-for-veincam-the-advanced-way)
    - [Preparing the SD Card](#preparing-the-sd-card)
    - [Configuring the PiJuice](#configuring-the-pijuice)
    - [Installing OpenCV](#installing-opencv)
        - [Preparing the Filesystem](#preparing-the-filesystem)
        - [Installing the OpenCV Dependencies](#installing-the-opencv-dependencies)
    - [Installing OpenCV](#installing-opencv)
    - [Preparing the Python Compiler](#preparing-the-python-compiler)
    - [Compiling and Installing](#compiling-and-installing)
    - [Wireless Hotspot Configuration](#wireless-hotspot-configuration)
6. [Preparing for VeinCam Autostart](#preparing-for-veincam-autostart)
7. [Running the VeinCam Software](#running-the-veincam-software)
8. [Encasing the VeinCam](#encasing-the-veincam)

# Required Hardware
- [Raspberry Pi 3 (Model B+)](https://www.raspberrypi.org/products/raspberry-pi-3-model-b-plus/)
- [Raspberry PiCam NoIR](https://www.raspberrypi.org/products/pi-noir-camera-v2/)
- PiJuice HAT for the Raspberry Pi
- ~750nm Infrared Filter
- 6 850nm Infrared LEDs
- 65mm x 95mm Veraboard (may need to cut a slightly larger one down)
- 16GB MicroSD Card
- 8 3mmx5mm diameter disk magnets
- 3 20mmx10mmx3mm cuboid magnets
- Micro USB phone charger (2.1A output required)

# Assembling the Raspberry Pi
Attach the NoIR Camera module to the Raspberry Pi (RPi). To do this, disengage the lock on the port by lifting the edge tabs until you feel a click. The ribbon cable should be orientated as seen in the image below:

<div class="row">
  <div class="column">
    
  </div>
  <div class="column">
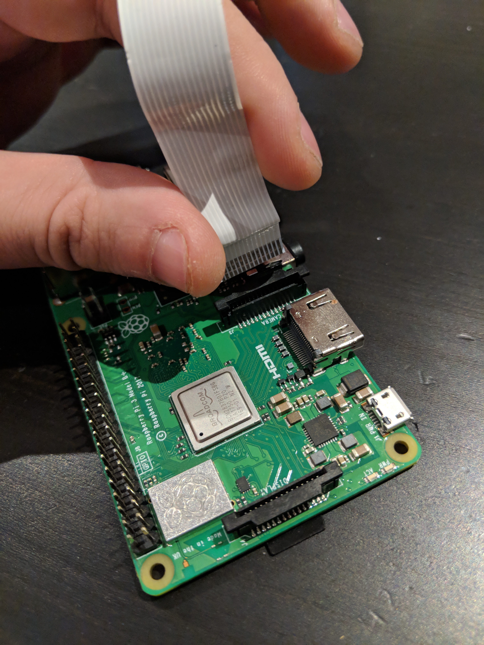
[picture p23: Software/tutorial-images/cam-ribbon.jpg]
    
  </div>
</div>

Once the cable is firmly seated, press down on the edge tabs once again until you feel that click. Place the camera module down like in the next image, where the ribbon cable sits over the rear ports of the RPi. Put a slight kink in the ribbon cable support (Blue plastic) to help keep the cable flat.

<div class="row">
  <div class="column">
    
  </div>
  <div class="column">
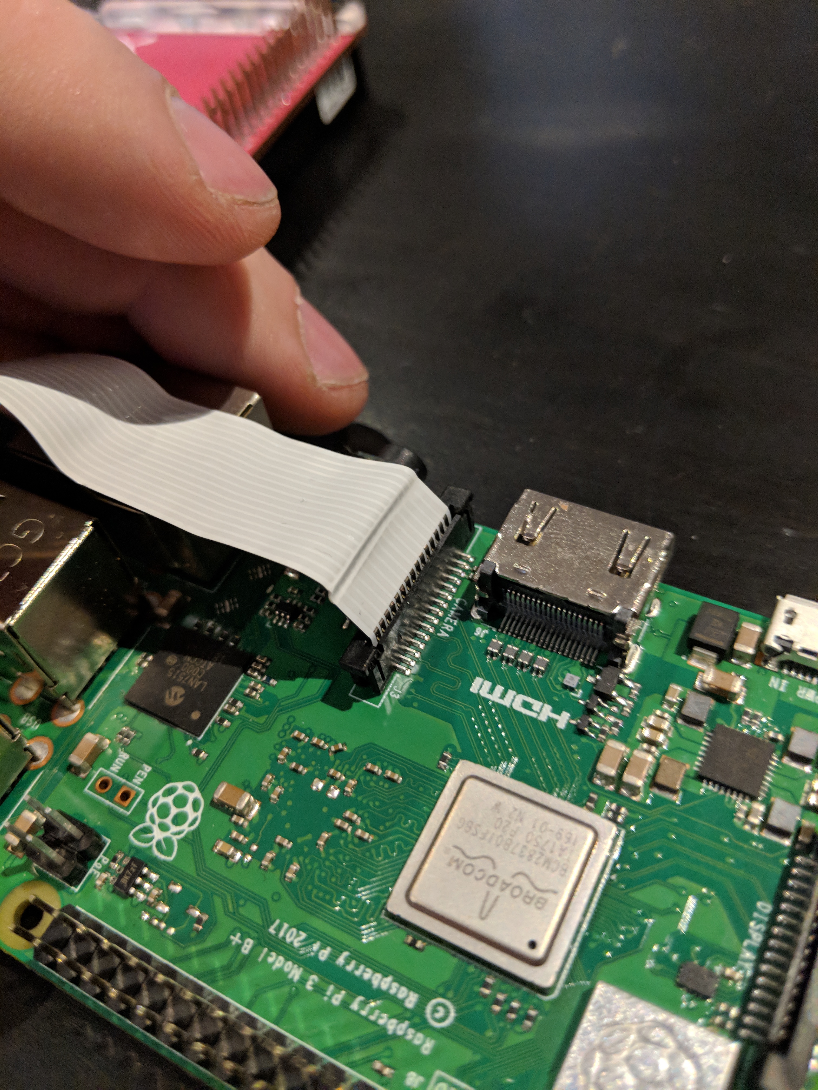
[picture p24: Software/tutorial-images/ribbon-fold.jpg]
    
  </div>
</div>

Install the PiJuice HAT onto the RPi. ensure that the pins on the RPi are aligned to the header on the underside of the PiJuice. The screw posts on the PiJuice should all align with the holes on the RPi board. Make sure you move the camera ribbon cable out of the way of the screw posts near the ports. Damage to the cable can result in the camera being unusable.

<div class="row">
  <div class="column">
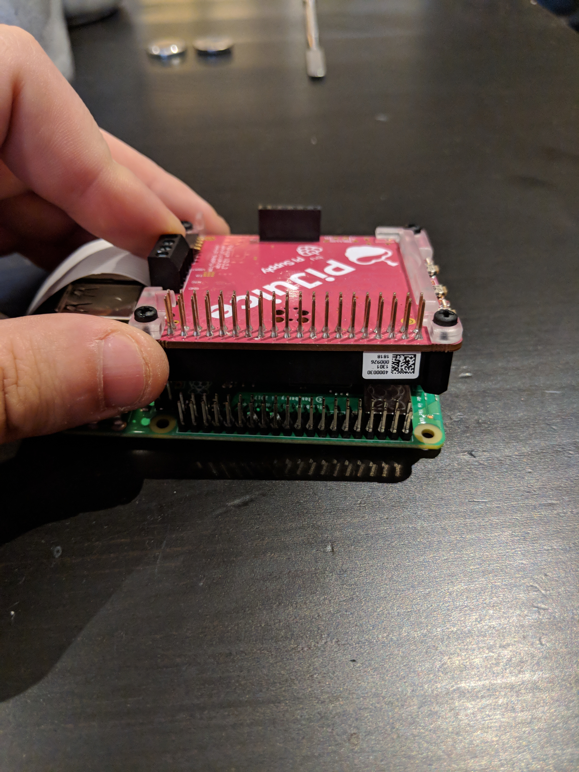
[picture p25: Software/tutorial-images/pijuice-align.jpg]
    
  </div>
  <div class="column">
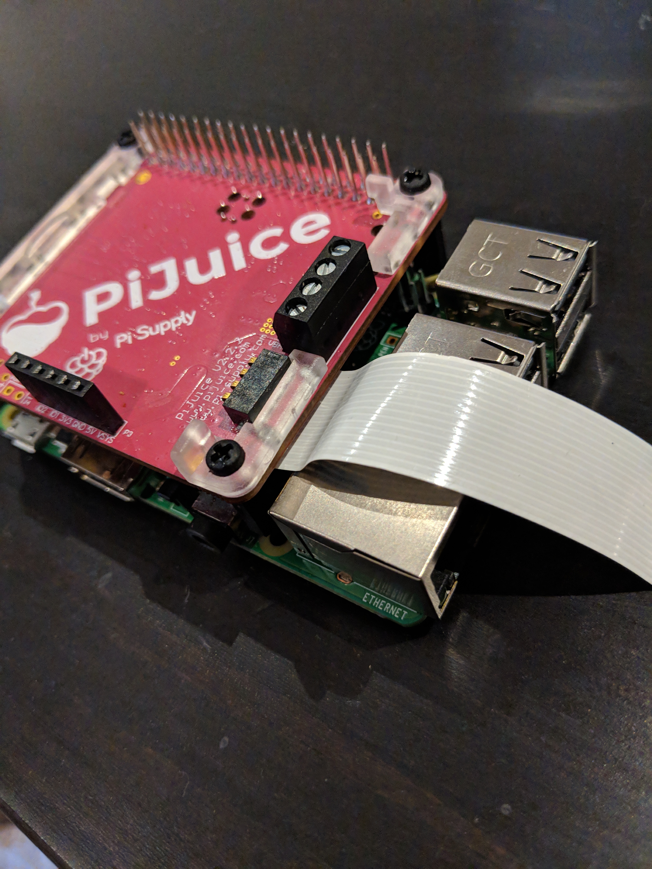
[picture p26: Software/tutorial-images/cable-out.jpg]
    
  </div>
</div>

# Assembling the LED Array (WARNING: BURN HAZARD)
WARNING: There is great potential to burn yourself if you are not skilled in electronic soldering. Seek assistance as required!

Study the image below carefully. the prototyping board should have grid references for you to use. each LED must have a 220-ohm resistor attached to the positive (longer) leg, which is attached to a 5v voltage rail, while the negative LED is connected to a ground rail.

<div class="row">
  <div class="column">
    
  </div>
  <div class="column">
    
  </div>
</div>

Connect the Positive wire to the 5V header on the PiJuice, and the negative wire to the Ground Pin.

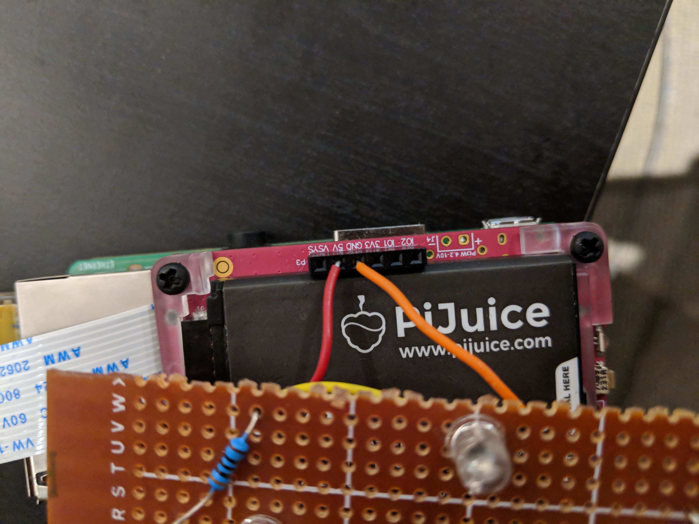
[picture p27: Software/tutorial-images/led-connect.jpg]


# Preparing The Raspberry Pi for VeinCam (The Quick Way)
Download a program called [Etcher](https://etcher.io/) which is available on all desktop platforms. Etcher is a simple tool to flash ISO files to USBs and SD Cards. Also download the ISO file found [here](https://drive.google.com/file/d/1dWCqL9uJaJdlJALsTNYojDlLWLJRyn4l/view?usp=sharing) and save it to you computer.

Run Etcher once it is installed, and insert the microSD card into your computer - most microSD cards come with an SD Card adapter to make this easier, and Etcher will auto-detect the card within a few seconds. Click the 'Select Image' button and navigate to where you downloaded and saved the ISO file.

The 'Flash!' button should now be available. Click it and wait for the flashing process to complete. Do not touch the SD card while this completes as you can corrupt the card and have to start again. Make sure your computer does not go to sleep or turn off during this process as well.

When the flash is complete, Etcher will prompt you with 'Flash Complete'. Remove the card from your computer and put it into the microSD slot on the underside of the RPi. Connect the power cable to the PiJuice and press the button closest to the charger. See [The User Guide](/User-Manual.md) on how to connect to the device with your personal device.

# Preparing The Raspberry Pi for VeinCam (The Advanced Way)
Install the Raspbian operating system. At time of writing, Stretch is the latest version, and can be downloaded from the Raspberry Pi Website. You can install either the full desktop version, or the lite version for those who are familiar with navigating through a Command Line Interface. You will need a Desktop/Laptop for the remainder of the guide (Windows, Mac or Linux), one with an microSD/SD Card slot, otherwise you will also require a USB adapter.

## Preparing the SD Card
This guide uses the Full Desktop version. Download the Raspbian ISO file [Here](https://www.raspberrypi.org/downloads/) and save it to your computer. Download a program called [Etcher](https://etcher.io/) which is available on all desktop platforms. Etcher is a simple tool to flash ISO files to USBs and SD Cards.

Run Etcher once it is installed, and insert the microSD card into your computer - most microSD cards come with an SD Card adapter to make this easier, and Etcher will auto-detect the card within a few seconds. Click the 'Select Image' button and navigate to where you downloaded and saved the ISO file.

The 'Flash!' button should now be available. Click it and wait for the flashing process to complete. Do not touch the SD card while this completes as you can corrupt the card and have to start again. Make sure your computer does not go to sleep or turn off during this process as well.

When the flash is complete, Etcher will prompt you with 'Flash Complete'. Remove the card from your computer and put it into the microSD slot on the underside of the RPi. Connect the necessary cables to the RPi - you will need a keyboard, mouse, ethernet cable (connected to your router) and a monitor connected via HDMI.

Once this is done, connect power to the Micro USB port on the PiJuice (this will start charging the battery) and press the small button closest to the USB port. A red LED on the RPi board will illuminate, indicating it has turned on. You will see it booting up on your screen, and within 15 seconds it will display the RPi desktop with the 'Welcome to Raspberry Pi' dialog box. this is a first run program to configure your RPi. Step through and fill in the required information. DO NOT configure a Wi-Fi network to the device, as it will be overridden by the Wi-Fi hotspot software and can cause issues.

## Configuring the PiJuice
Open up a terminal window, and run the following command
```
sudo apt-get install pijuice-gui
```
This will install the software required to configure the PiJuice.

**set up for switches**

## Installing OpenCV
### Preparing the Filesystem
This install guide follows what is detailed [on this page](https://www.pyimagesearch.com/2017/09/04/raspbian-stretch-install-opencv-3-python-on-your-raspberry-pi/). Images in this guide are courtesy of the original guide.
First expand the file system to fill the entire SD Card. In the terminal:
Type
```
sudo raspi-config
```

Navigate to **7. Advanced Options > A1 Expand Filesystem** and step through any prompts. Reboot the Pi if prompted to do so after expanding the filesystem, otherwise type the following into the terminal.
```
sudo reboot
```

Once rebooted, the file system should fill the SD card. You can use ```df -h``` to check this. ```/dev/root``` should be a similar size to the SD Card.

Some space can be freed from the default install by removing some software. Wolfram and Libreoffice will not be used on the platform, and takes up around a 1GB of storage. Use the code below to remove these applications from the system:
```
sudo apt-get purge wolfram-engine
sudo apt-get purge libreoffice*
sudo apt-get clean
sudo apt-get autoremove
```
the purge commands will remove the core applications, while the clean and autoremove clear out any links to the applications, and remove any unused dependencies for more free space. this may take several minutes to complete.

### Installing the OpenCV Dependencies
Especially if you are starting from a fresh install of Raspbian, it is crucial to update the system, to ensure the repository and core system functions are up to date.
```
sudo apt-get update && sudo apt-get upgrade
```
This command will update the repository first, then update the system using the now updated repository. again, this may take several minutes to complete - depending on your Pi and internet connection.

Next is to install the compiling packages
```
sudo apt-get install build-essential cmake pkg-config
```

the next commands install various packages to help compile OpenCV.
```
sudo apt-get install libjpeg-dev libtiff5-dev libjasper-dev libpng12-dev
sudo apt-get install libavcodec-dev libavformat-dev libswscale-dev libv4l-dev
sudo apt-get install libxvidcore-dev libx264-dev
sudo apt-get install libgtk2.0-dev libgtk-3-dev
sudo apt-get install libatlas-base-dev gfortran
sudo apt-get install python2.7-dev python3-dev
```
Note that each line has to be run individually, as some packages have dependencies located in the command above it.

## Downloading OpenCV
There are 2 packages that are required for download, in order of OpenCV to run. you can grab them bun running the commands below:
```
cd ~
wget -O opencv.zip https://github.com/Itseez/opencv/archive/3.4.2.zip
wget -O opencv_contrib.zip https://github.com/Itseez/opencv_contrib/archive/3.4.2.zip
unzip opencv.zip
unzip opencv_contrib.zip
```
At the time of writing, version 3.4.2 is the latest version. If there is a later version, simply change the version numbers. Note that the version numbers must match for these packages to compile.

## Preparing the Python Compiler
Before we get started, we need a Python Package Manager
```
wget https://bootstrap.pypa.io/get-pip.py
sudo python get-pip.py
sudo python3 get-pip.py
```
The package manager is used to help maintain Python-specific packages, in the same way that the Raspbian Repository maintains software packages for the OS. One particular package we need is the Virtual Environment package and dependencies. The Virtual Environment enables the ability to create sandboxed environments where Python can execute without interference from other python packages. (like having individual users on one system, where documents and such do not collide with one another).

We can install these packages like so:
```
sudo pip install virtualenv virtualenvwrapper
sudo rm -rf ~/.cache/pip
```
We will also need to update the terminal profile to load these packages for quick reference. Use a terminal editor such as nano to edit the following file:
```
sudo nano ~/.profile
```
and add the following lines to the bottom of the file:
```
# virtualenv and virtualenvwrapper
export WORKON_HOME=$HOME/.virtualenvs
export VIRTUALENVWRAPPER_PYTHON=/usr/bin/python3
source /usr/local/bin/virtualenvwrapper.sh
```
Reload the terminal profile simply by running the command:
```
source ~/.profile
```
You will see the terminal load in the Python packages we installed previously.
Now we create the virtual environment. Depending what version of python you wish to run with, execute one of the following commands:
```
# Python 2.7
mkvirtualenv cv -p python2

# Python 3.5
mkvirtualenv cv -p python3
```

Upon creation of the environment, it's name (in this case is cv) will appear in parentheses as a prefix to the command entry in the terminal, which can be seen below.

virtual environment indicator

If this is not the case, use the commands below to enter the virtual environment
```
source ~/.profile
workon cv
```

**workon cv** is the command that enters the environment. Prior to this, we reload the profile to ensure the virtual environment packages are loaded into the terminal.

Next we need to install NumPy, a package used for numerical processing, which will in part will allow for numerical image processing for our automated controls. (BETTER EXPAND THIS)
```
pip install numpy
```

## Compiling and Installing
Now its time for the installation. But first we need to compile the software. **Note that it will take more than an hour to successfully compile**. Before we start, make sure you are in the virtual environment
```
workon cv
```
Run the following commands to create the build file for OpenCV. Note that if you are using a different version of OpenCV than what is used in this guide, be sure to change the version numbers otherwise it will not compile.
```
cd ~/opencv-3.4.2/
mkdir build
cd build
cmake -D CMAKE_BUILD_TYPE=RELEASE \
    -D CMAKE_INSTALL_PREFIX=/usr/local \
    -D INSTALL_PYTHON_EXAMPLES=ON \
    -D OPENCV_EXTRA_MODULES_PATH=~/opencv_contrib-3.4.2/modules \
    -D BUILD_EXAMPLES=ON ..
```
Examine the output to ensure that Interpreter, Libraries, NumPy and packages path fields of the output are pointing to the correct directories. It should look similar to the images below, depending on the Python version you are using. In this case, we are using Python 3. We can also see the Python 2 links above the red box.

Python 3 links

Now we need to change the file swap size. the default used by Raspbian is small, and could cause compilation errors. run the command below to open up the swap file configuration file in nano:
```
sudo nano /etc/dphys-swapfile
```

Look for the CONF_SWAPSIZE parameter from 100 to 1024. this will increase the swap file to 1GB. Note that we will need to change it back after compilation, as it could fill up the SD card over time, very quickly. the parameter should now look like this:
```
CONF_SWAPSIZE=1024
```
Once this is done, we need to ensure that the change takes effect. Run the commands below to restart the swapfile service.
```
sudo /etc/init.d/dphys-swapfile stop
sudo /etc/init.d/dphys-swapfile start
```
Now we can start the compilation. Again, be aware that the compilation process will take more than an hour to complete. you also should still be in the build directory.
```
cd ~/opencv-3.4.2/build
make -j4
```
When the compilation is complete, we can start the install onto the Pi.
```
sudo make install
sudo ldconfig
```

Lastly, execute one of the following blocks of code, depending on the version of Python you compiled with. These blocks create the symbolic link between the OpenCV packages and the virtual environment we created earlier.

```
# Python 2.7
cd ~/.virtualenvs/cv/lib/python2.7/site-packages/
ln -s /usr/local/lib/python2.7/site-packages/cv2.so cv2.so
```

```
# Python 3.5
cd /usr/local/lib/python3.5/site-packages/
sudo mv cv2.cpython-35m-arm-linux-gnueabihf.so cv2.so

cd ~/.virtualenvs/cv/lib/python3.5/site-packages/
ln -s /usr/local/lib/python3.5/site-packages/cv2.so cv2.so
```
## Wireless Hotspot Configuration
This is mainly takes one command to fully configure using the [RaspAP Utility](https://github.com/billz/raspap-webgui). This utility installs the required dependencies and configures the Raspberry Pi into a self-serving Internet access point. The advantage to this is that it can allow connections from multiple devices and allow them 'Internet' access, like a modem would. Internet can also be passed through the RasPi via its on board ethernet port.

Before setup, disconnect any wireless networks the device may already be connected to, and plug in an ethernet cable. Execute the command below and it will download the required files and start the install.

```
wget -q https://git.io/voEUQ -O /tmp/raspap && bash /tmp/raspap
```

It will prompt you for input, accept them by typing 'y' and hitting enter (as some prompts are defaulted to 'no' when you hit enter). The Pi will need a reboot when prompted to do so. Once it has rebooted, you should see a new WiFi called ``raspi-webgui``. This is the newly configured access point. The default parameters are as below:
* SSID: raspi-webgui
* Password: ChangeMe
* IP address: 10.3.141.1
  - Login Username: admin
  - Login Password: secret
  - DHCP range: 10.3.141.50 to 10.3.141.255

You can log into the web interface, and change parameters by using the login details listed above. These are the default parameters, so you may wish to change them. Below are the parameters we used.
* SSID: VeinCam
* Password: ANUVeinCam
* Channel: 6

## Preparing for VeinCam AutoStart
During our development, we encountered an error where the bash profile would not autorun on user log in. We determined that this was likely due to the OS was preconfigured to log into the desktop environment automatically, and the profile script does not automatically load.

To fix this, we need to switch to the CLI environment for boot, and back again. to do this, open a terminal and execute the command
```
sudo raspi-config
```
and navigate to **"3 Boot options > B1 Desktop / CLI > Console Autologin"** and go finish. it will ask you to reboot. Accept and you will be booted into the command line interface. Run the config command again and go to **"3 Boot options > B1 Desktop / CLI > Desktop Autologin"** this time, and reboot. This should allow the profile to autoload on user login.

## Running the VeinCam Software
Ensure you are in the OpenCV environment:
```
source ~/,profile
workon cv
```
and run the next 2 commands:
```
pip3 install flask
pip3 install picamera
```
These are the last of the software required to run the VeinCam software - Flask is a python framework that extends what python can do, and is useful in our case to convert HTML into python commands (loading the web stream and controlling its parameters). The picamera module is for the camera itself, as the full library is not present within the python environment.

Download our [final code archive](Software/Final.zip) and save them to the home directory (/home/pi).

In a terminal, run the below command
```
sudo nano ~/.profile
```
and add these two lines to the bottom of the file
```
workon cv
bash launcher.sh
```
Reboot your device, and you should be able to connect to it with your personal device using the settings you configured during [the Hotspot configuration](#wireless-hotspot-configuration).

## Encasing The VeinCam
With everything else complete, the only thing left is to put it into a case. [Our custom case](/CAD-Drawings/v2.3) is designed to house all the components comfortably. You can download the design and 3D print it yourself, have someone help you, or get in contact with a 3D printing service.

Or you can create your own! Internal compartment dimensions are as follows:

* 100mm long
* 65mm deep
* 40mm high

we used small neodymium disk magnets to secure the lid to the main compartment, and provides a nice snap shut fit. Check out the final drawings in our repository!

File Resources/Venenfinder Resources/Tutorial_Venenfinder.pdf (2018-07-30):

Venenfinder – a DIY medical assistive device.
Elias Stoetzer (12), Lucie Ettlinger (16), Myrijam Stoetzer (16)

Venenfinder – a DIY medical assistive device.

This tutorial describes how to build the „Venenfinder“ (vein-finder) from scratch. It is a medical assistive device that was developed by us to make it easier for medical stuff as well as people with chronic illnesses to get vein access.

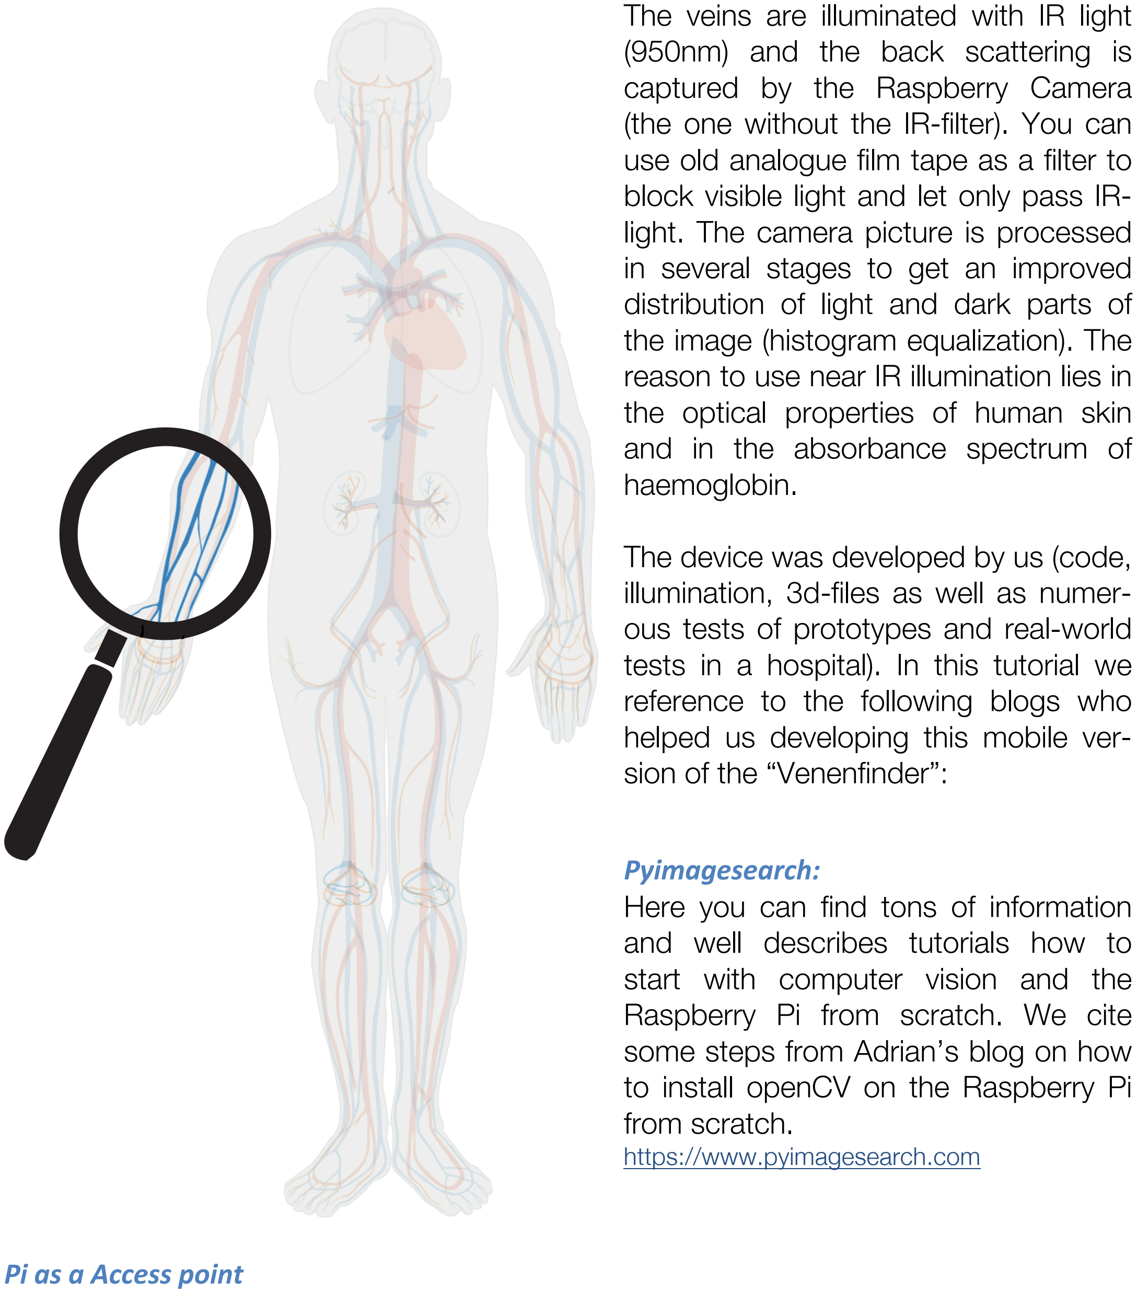
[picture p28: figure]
The veins are illuminated with IR light (950nm) and the back scattering is captured by the Raspberry Camera; light. The camera picture is processed in several stages to get an improved distribution of light and dark parts of the image (histogram equalization). The; the optical properties of human skin and in the absorbance spectrum of haemoglobin.; The device was developed by us (code,; ous tests of prototypes and real-world; reference to the following blogs who helped us developing this mobile ver- sion of the “Venenfinder”: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

(the one without the IR-filter). You can use old analogue film tape as a filter to block visible light and let only pass IR-

reason to use near IR illumination lies in

illumination, 3d-files as well as numer-

tests in a hospital). In this tutorial we

If you want to stream the calculated image to your smartphone, TV or tablet, you either need to integrate the Raspberry into your local Wifi network – or just start a new one. We don’t want the user to have to deal with editing wifi settings on a terminal session, so we just decided to turn the Pi into a Hotspot. Here we followed Phil Martin’s blog on how to use the Raspberry as a Wifi Accesspoint:
https://frillip.com/using-your-raspberry-pi-3-as-a-wifi-access-point-with-hostapd/

Rotary encoder:
Since you need a way to change the setting of the image enhancement, we decided to use rotary encoders. These are basically just 2 switches and they sequence they close and open tells you the direction the knob was turned.
We soldered 3 rotary encoders to a little board and created a Raspberry HAT on our own. For the code we used:
http://www.bobrathbone.com/raspberrypi/Raspberry%20Rotary%20Encoders.pdf

Streaming Server in Python:
We used some code from Igor Maculan – he programmed a Simple Python Motion Jpeg (mjpeg) Server using a webcam, and we changed it to Picam, added the encoder and display of parameters. Original Code:
https://gist.github.com/n3wtron/4624820

## Install / Compile Softwarecomponents

1. download Jessie (full) from Raspberri.org (Version 2017-04-10)
2. unzip file and write the image to an SD-Card (e.g. using Apple Pi-Baker or other tools; see e.g. https://www.raspberrypi.org/documentation/installation/installingimages/)
3. start the system with the new sd-card and configure it according to... http://www.pyimagesearch.com/2016/04/18/install-guide-raspberry-pi-3-raspbian-jessie-opencv-3/
4. Make sure network connections work (WiFi or LAN) – you need to download software packets

Steps to install the Software, OS, Network

Follow the steps in Adrian’s tutorial http://www.pyimagesearch.com/2015/10/26/howto-install-opencv-3-on-raspbian-jessie/

1. expand filesystem (automatic)
2. updates: (sudo apt-get update & sudo apt-get upgrade)
3. install the packages as described, but download opencv3.2 and additions for 3.2

Install packages:
developer tools:
sudo apt-get install build-essential git cmake pkg-config
image I/O packages
sudo apt-get install libjpeg-dev libtiff5-dev libjasper-dev libpng12-dev

video I/O packages:
sudo apt-get install libavcodec-dev libavformat-dev libswscale-dev libv4ldev
sudo apt-get install libxvidcore-dev libx264-dev
display images, gui etc:
sudo apt-get install libgtk2.0-dev
extra optimation for matrix operations:
sudo apt-get install libatlas-base-dev gfortran
Python 2.7 und 3 header files:
sudo apt-get install python2.7-dev python3-dev
Source-Files:
wget -O opencv.zip https://github.com/Itseez/opencv/archive/3.2.0.zip unzip opencv.zip

wget -O opencv_contrib.zip https://github.com/Itseez/opencv_contrib/archive/3.2.0.zip
unzip opencv_contrib.zip
python package manager
wget https://bootstrap.pypa.io/get-pip.py sudo python get-pip.py
install numpy (numerical python)
pip install numpy
compile opencv
cd ~/opencv-3.2.0/
mkdir build
cd build
cmake -D CMAKE_BUILD_TYPE=RELEASE \
-D CMAKE_INSTALL_PREFIX=/usr/local \
-D INSTALL_PYTHON_EXAMPLES=ON \
-D OPENCV_EXTRA_MODULES_PATH=~/opencv_contrib-3.2.0/modules \ -D BUILD_EXAMPLES=ON ..

make -j4
(This takes a good 45-60min).

Now openCV should be installed with all the necessary additions. Please test it by rebooting and starting Python 2:
sudo shutdown -r now
After reboot and login start Python interpreter either by choosing IDLE-Python 2 from program menu or by typing into terminal:
python

>>>import cv2
(should produce no errors)

Hardware, 3D-files etc.

For the hardware you simply need to print the stl-files according to your 3D-Printer’s software. The case is designed to fit the Raspberry Pi3 with the three encoders at-

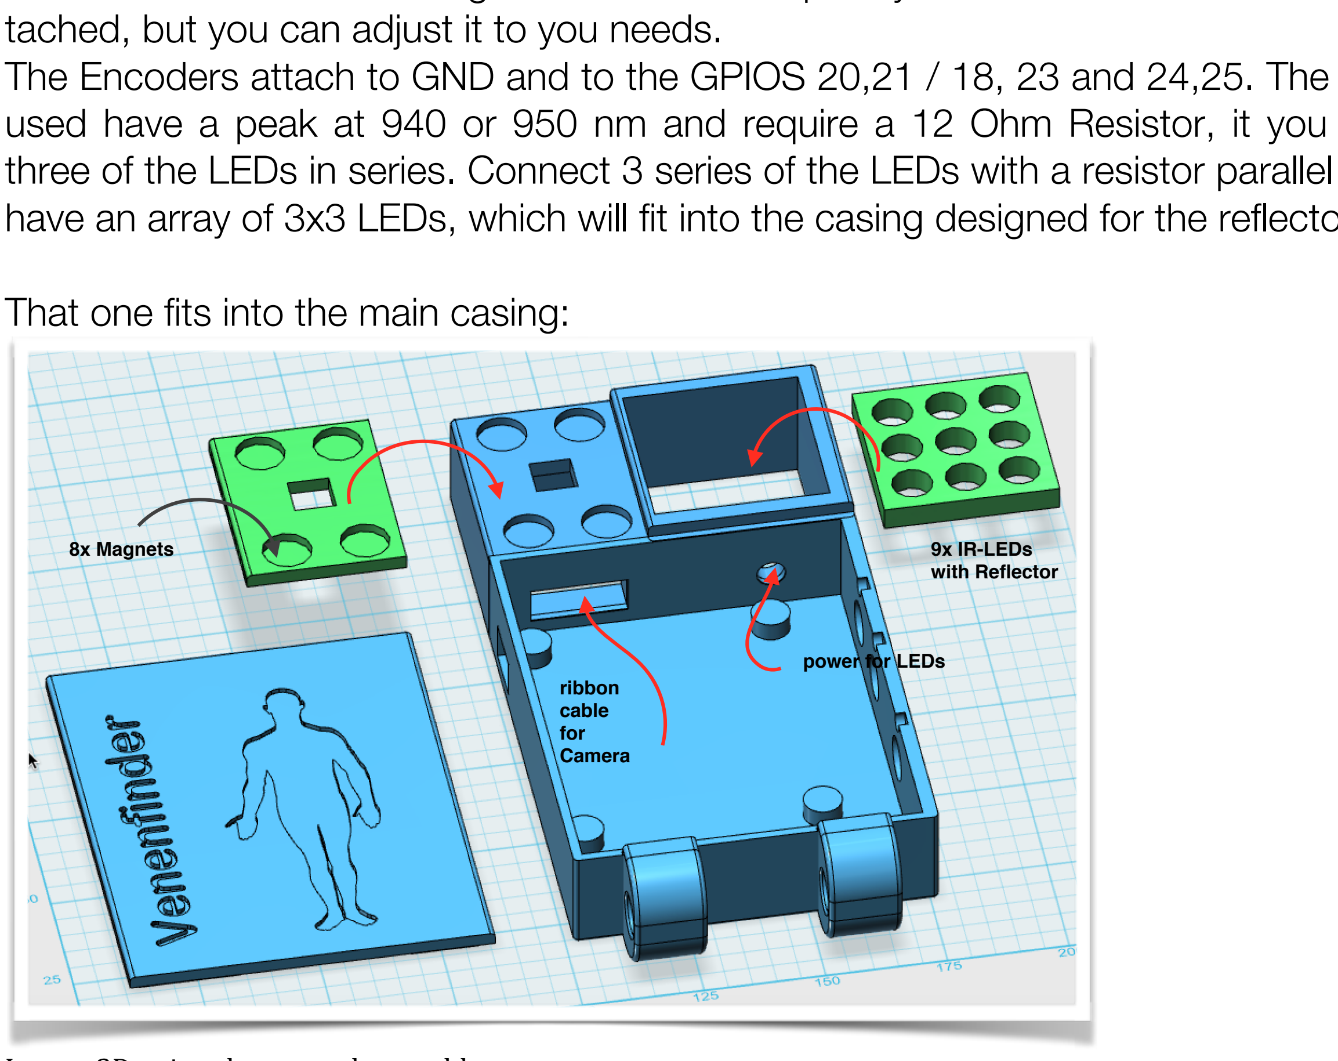
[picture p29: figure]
That one fits into the main casing:; 8x Magnets; 9x IR-LEDs; with Reflector; ribbon cable for Camera; power for LEDs

tached, but you can adjust it to you needs.
The Encoders attach to GND and to the GPIOS 20,21 / 18, 23 and 24,25. The IR-LEDs used have a peak at 940 or 950 nm and require a 12 Ohm Resistor, it you connect three of the LEDs in series. Connect 3 series of the LEDs with a resistor parallel and you have an array of 3x3 LEDs, which will fit into the casing designed for the reflectors.

Image: 3D-printed parts and assembly

Print the cover and the main casing with support; the adapter for the filter (analogue film tape) and IR reflector matrix won’t need support.

The circuit diagram for connecting LEDs and encoders:

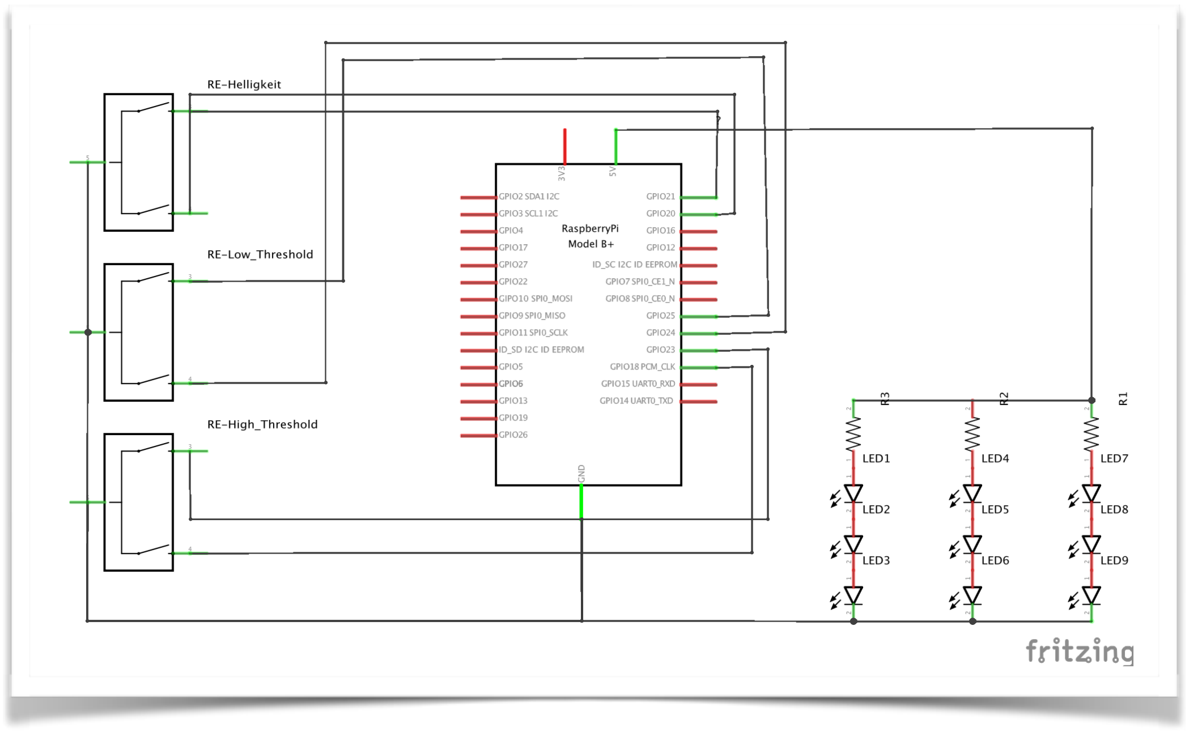
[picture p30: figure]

For our mobile version of the Venenfinder we used a piece of strip board, but if you want to build your own circuit board please keep in mind you may need to change the case to fit yours in…

Putting it all together: Wifi Access-Point, Autostart etc.

You can find the latest version of Venenfinder on Myrijam’s github page, including the code (Python script) and the 3d-files. All you need to do is to clone the git to your raspberry pi (or your regular computer to work with the 3d-files). https://github.com/Myrijam/Venenfinder
Server-Installation (Python)
Python already includes a simple http server you can use. It is just a little line of code to import the corresponding libraries into your python code (don’t run this in terminal):
from BaseHTTPServer import BaseHTTPRequestHandler,HTTPServer
from SocketServer import ThreadingMixIn

Wifi-Configuration (
These steps are mainly a short excerpt from Phil Martin’s blog:

Install hostapd (which will give you the ability to run an Accesspoint with building Wifi) and dnsmasq (combined DNS and DHCP Server):
sudo apt-get install dnsmasq hostapd

Edit the WLAN0-interface (build-in Wifi) preferences by using an editor on the commandline:
sudo nano /etc/dhcpcd.conf

add this line at the bottom, before any instructions starting with “interface” (if there are any)
denyinterfaces wlan0
Accesspoint needs a fixed (static) IP, so that the QR-Codes can work on the back of the device. Open this file and edit the section starting with WLAN0:
sudo nano /etc/network/interfaces
It should look like:
allow-hotplug wlan0
iface wlan0 inet static
address 192.168.42.1
netmask 255.255.255.0

Now you can restart the dhcp-service and reload the changed configuration:
sudo service dhcpcd restart
sudo ifdown wlan0; sudo ifup wlan0
Now the hostapd needs to be configured:

Create/edit the file by this command:
sudo nano /etc/hostapd/hostapd.conf
This is the content of hostapd.conf

# This is the name of the WiFi interface we configured above interface=wlan0

# Use the nl80211 driver with the brcmfmac driver driver=nl80211

# This is the name of the network ssid=Venenfinder

# Use the 2.4GHz band

hw_mode=g
# Use channel 6

channel=6
# Enable 802.11n

ieee80211n=1
# Enable WMM

wmm_enabled=1
# Enable 40MHz channels with 20ns guard interval ht_capab=[HT40][SHORT-GI-20][DSSS_CCK-40]

# Accept all MAC addresses

macaddr_acl=0
# Use WPA authentication

auth_algs=1
# Require clients to know the network name ignore_broadcast_ssid=0

# Use WPA2

wpa=2
# Use a pre-shared key

wpa_key_mgmt=WPA-PSK
# The network passphrase

wpa_passphrase=vene1181
# Use AES, instead of TKIP

rsn_pairwise=CCMP

Please pay attention to the statements in bold – these are SSID and PW of the device. It is not an elegant solution to hard-code any password in, but in the rush for the final we could not find an easier configuration –so please change them!

Now tell the hostapd where to look for the config file:
sudo nano /etc/default/hostapd

change the line from #DAEMON_CONF="" to DAEMON_CONF="/etc/hostapd/hostapd.conf"

Next step is to change the config of DNSMASQ. Phil Martin suggests to copy the preconfigured file and keep it that way before creating a new one:

sudo mv /etc/dnsmasq.conf /etc/dnsmasq.conf.orig

And then create a new config file:
sudo nano /etc/dnsmasq.conf
Paste the following content:
interface=wlan0 | # Use interface wlan0
listen-address=192.168.42.1 | # Address to listen on
bind-interfaces | # Bind to the interface
server=8.8.8.8 | # Forward DNS requests to Google DNS

domain-needed | # Don't forward short names
bogus-priv | # Never forward non-routed address spaces.
dhcp-range=192.168.42.10,192.168.42.150,12h # Clients IP range and time
Now it is time to set the rules for managing traffic on the interfaces:
sudo nano /etc/sysctl.conf

Search fort he line containing net.ipv4.ip_forward=1 and remove the # from the beginning of the line. Enable this rule by:
sudo sh -c "echo 1 > /proc/sys/net/ipv4/ip_forward"
The following commands define the traffic routing between Wifi and Ethernet; it is probably not necessary for this special use case:
sudo iptables -t nat -A POSTROUTING -o eth0 -j MASQUERADE
sudo | iptables | -A FORWARD | -i | eth0 | -o wlan0 | -m state | --state | RELAT-
ED,ESTABLISHED -j ACCEPT
sudo iptables -A FORWARD -i wlan0 -o eth0 -j ACCEPT

These rules need to run every time at bootup, so this saves the rules for later use:
sudo sh -c "iptables-save > /etc/iptables.ipv4.nat"

Now run the following command to enable restoring these rules at bootup:
sudo nano /etc/rc.local

Just before the line exit 0 enter the following command:
iptables-restore < /etc/iptables.ipv4.nat

Now you just need to restart the corresponding services:
sudo service hostapd start
sudo service dnsmasq start
Now the Raspberry 3 should work as an access point, providing a network with the specified SSID (“Venenfinder”) and the PSK (“vene1181”).
To make sure the device runs the Venenfinder-Python code at reboot, please refer to the following section.
Autostart
Use the following command to add autostart to the Python Code from Venenfinder :
sudo nano /etc/profile

And put a last line to the script:
python /home/pi/Venenfinder/Venenfinder.py
Rebooting the Raspberry will start the Venenfinder now :-)

## Connecting…

You can scan these QR-Codes to connect to Venenfinder, given you used the combination of SSID and PSK provided in this tutorial:

QR-Code for Wifi-Network

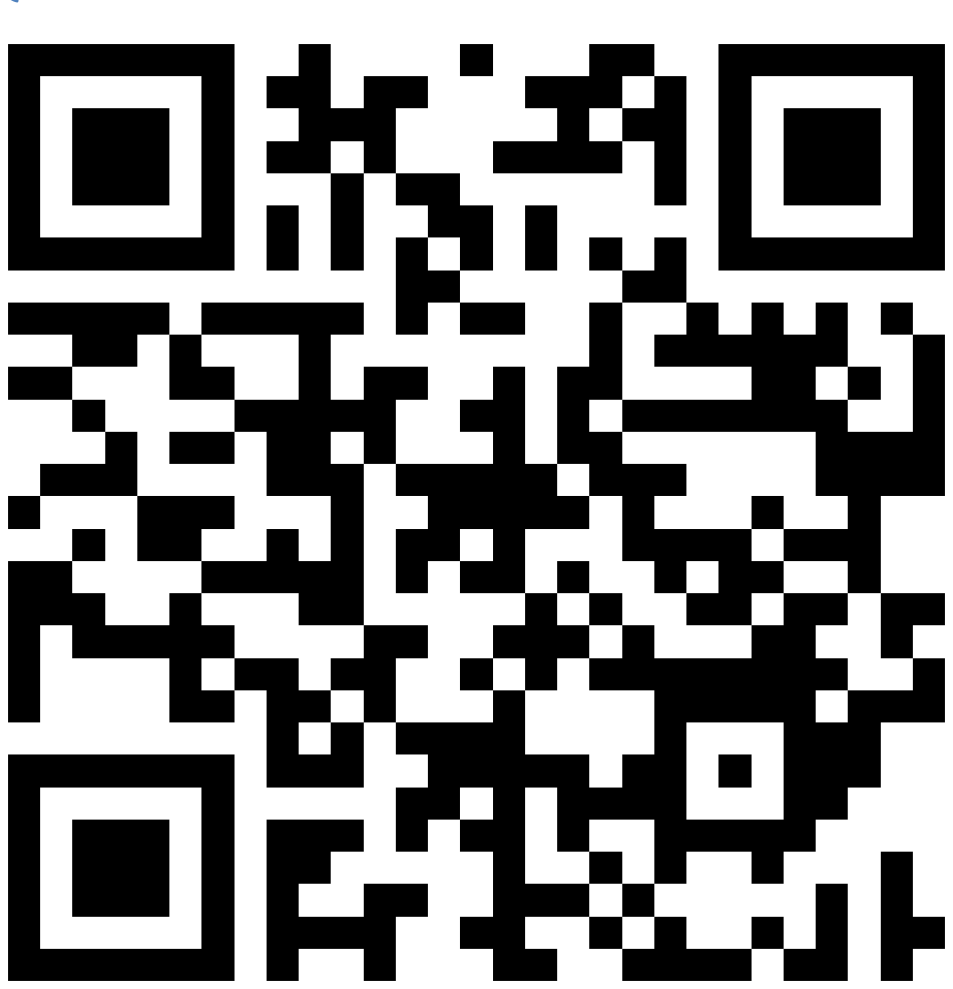
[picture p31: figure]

SSID: Venenfinder PSK: vene1181

QR-Code for Live-Streaming (Android, Computer):

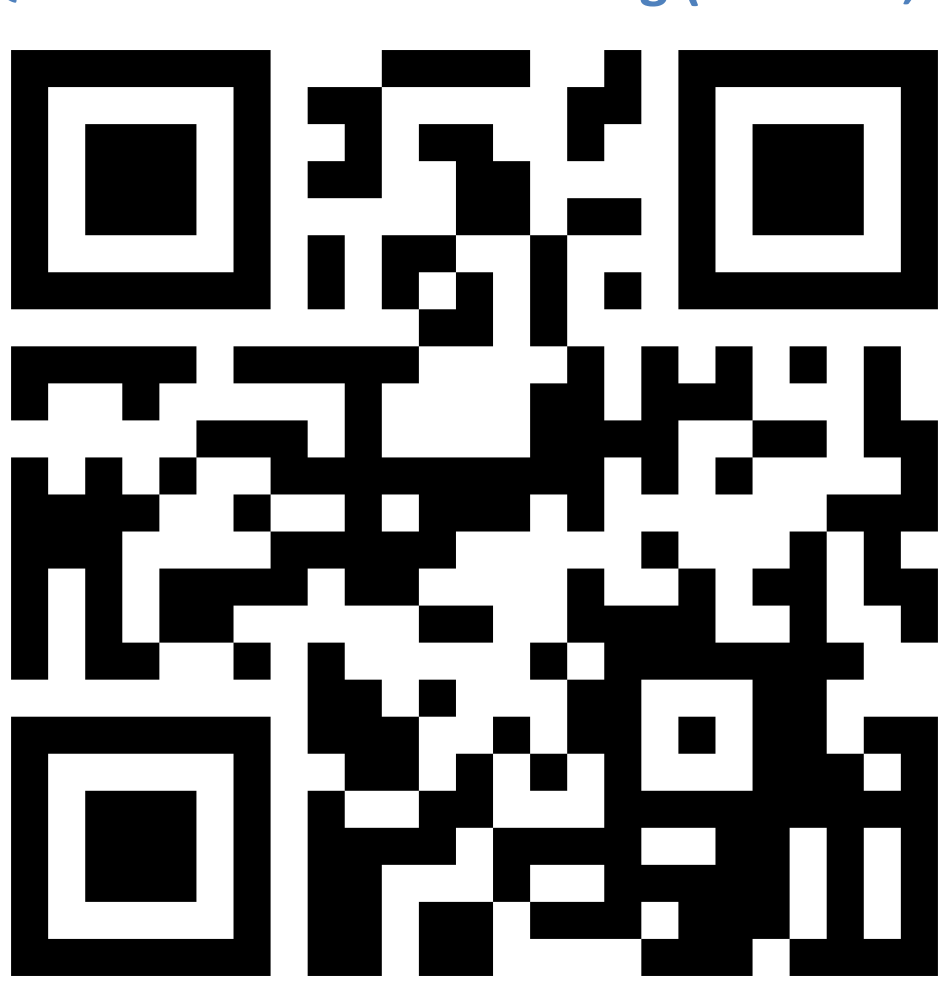
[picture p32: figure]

http://192.168.42.1:8080/cam.mjpg

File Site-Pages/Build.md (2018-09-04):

## Build
Right now while we are still working on developing the VeinCam this page is going to be a bit empty. When we have a better working prototype this page will be a guide on how to build a VeinCam and install the software (also available here) to run it.

If you are interested in [contributing](/Site-Pages/Contribute.md) then get in [contact](/Site-Pages/Contact.md) with us because we'd love to have any feedback and input you could provide. For more details you can also visit our [repository on GitHub](https://github.com/chrisbodger/VeinCam).

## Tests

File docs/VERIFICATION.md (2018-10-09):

# Device Specification Verification
The prototype device must be verified against the specifications as developed from the [Requirements](REQUIREMENTS.md) to ensure a successful prototype. A series of tests have been created to verify the design:

## Tests
Test IDs correlate with specification IDs found in the [Requirements](REQUIREMENTS.md) document. At this stage venous puncture is not permitted for testing and there is no stand to address a number of specifications, though tests have been considered.

| ID | Device/User Testing | Test |
| --- | --- | --- |
| 1 | D | The estimated material cost of the prototype. This includes pre-purchased materials but does not include labour. |
| 2.1 | D | User judgement on the distance at which the picture is most in focus. |
| 2.2 | D | Device set to minimum and maximum height and must remain stable for at least 1 minute. |
| 2.3 | D | Device set to operate and not interfered with until failure or a 10 minute limit reached |
| 2.4 | D | Measure the time taken for the device to use a full charge when left to stream indefinitely. |
| 3.1 | D | User judgement of significant packet loss when increasing the distance from camera device to streaming device. |
| 3.2 | D | TBA |
| 4 | D | Measure the maximum dimensions of the prototype |
| 5.1 | U | A yes/no judgement of a user who teaches anatomy (or a similar subjects) on whether or not they would "use the device". |
| 5.2 | D | Measure the time taken from switching on the device to streaming |
| 5.3 | D | Test the stream on a number of different devices and OS (e.g. windows desktop, apple tablet etc.) |
| 6.1 | D | The number of steps of how to construct the device, dictated by an independent user being able to construct the device |
| 6.2 | U | Provide a set of instructions to an independent individual and measure how long it takes them to construct the device |
| 7.1-5 | U | A yes/no judgement from the user on whether veins can be clearly seen. Minimum sample size n=10 for each use case (dark complexion, high BMI, thick hair or tattoos covering veins) |
| 7.6 | U | Similar to above |

## Results Table Template
As prototypes are tested the results will be updated here. Raw data can be found [here](https://docs.google.com/spreadsheets/d/18sSy89GIRTKhPBCF92-t4Pr2AGmHzw_IFHvKGeLFWAo/edit?usp=sharing).

| ID | Specification | Metric | Benchmark | Result |
| --- | --- | --- | --- | --- |
| 1 | Total Cost | $ | <250 | |
| 2.1 | Camera Focal Length | mm | 300-500 | |
| 2.2 | Adjustable Set Height | mm | 300-500 | |
| 2.3 | Handsfree Operation | min | >5 | |
| 2.4 | Battery Life | min | >60 | |
| 3.1 | Wireless Range | m | >1 | |
| 3.2 | Stream Delay | ms | <1000 | |
| 4 | Form Factor | mm | <150 x 90 x 70 | |
| 5.1 | User Acceptance | % | >90 | |
| 5.2 | Boot Time | s | <15 | |
| 5.3 | OS Compatibility | # | >2 | |
| 6.1 | Construction Steps | # | <5 | |
| 6.2 | Construction Time | hrs | <2 | |
| 7.1 | Automatic Contrast Adjustment (for ideal scenario) | % | >90 | |
| 7.2 | Automatic Contrast Adjustment (for any complexion) | % | 80 | |
| 7.3 | Automatic Contrast Adjustment (for high BMI/obesity) | % | 80 | |
| 7.4 | Automatic Contrast Adjustment (for any amount of hair) | % | 80 | |
| 7.5 | Automatic Contrast Adjustment (for tattooed area) | % | 80 | |
| 7.6 | Visualise Vascular Blood Flow | % | 80 | |

## Change Log
| Date | Change | Justification |
| --- | --- | --- |
| 29/9/18 | Changes made in-line with requirements changes | Verification reflects requirements/specifications. |
| 29/9/18 | Added device/user testing specification. | Need to differentiate between what can be tested with/without ethics approval. Device testing will not require ethics approval while user testing would. |

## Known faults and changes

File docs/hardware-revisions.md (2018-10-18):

# Case Revisions

| Revision Number | Changes | Comments |
| :---: | :---: | :---: |
| 1.0 | Initial Design | Large and bulky, proof of concept |
| 1.1 | Adjusted the RPi mounting points, and the tolerances in the lid fit | Still large, but device sits relatively well. LED Array fits perfectly |
| 2.0 | Smaller, less gaps between RPi and wall, round internal edges, added array mounting lips to help hold larger PCBs | Charting port out of alignment, button holes were too close together |
| 2.1 | Button holes correctly spaced apart, aligned the charging port correctly | Print failed several times, seems to be overwritten by v2.2 |
| 2.2 | Adjustment to case, made more ergonomic, added compartment for magnetic mounts | Botton holes too low, slightly undersized |
| 2.3 | Raised the height of the buttons, made slightly larger | Concept, still needs to be printed and tested |

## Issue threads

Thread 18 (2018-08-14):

### ISSUE TITLE
AUDIT 1 - Stakeholder Analysis

### ISSUE THREAD

**Issue by chrisbodger** [chrisbodger/VeinCam#18]
Comments left regarding Stakeholder Analysis
- Definition should focus on people or groups instead of Project. perhaps include patients and medical professionals/hospitals

**Comment by steph-pratt** [comment]
Now in the Google Drive, I am unsure how to add it into the GitHub as a word doc if someone could please do that (or show me). I also have it in two formats - as list and as a table - can look and see which is better

**Comment by JoeyMcP** [comment]
Added to ConOps under Stakeholders heading.

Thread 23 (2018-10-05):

### ISSUE TITLE
Research into wavelengths of light

### ISSUE THREAD

**Issue by steph-pratt** [chrisbodger/VeinCam#23]
Ben mentioned in recent email we may want to add this to our area to research to help Alex and Chris select the best LEDs to employ. 

Links include:
- https://en.wikipedia.org/wiki/Near-infrared_window_in_biological_tissue
- https://en.wikipedia.org/wiki/Pulse_oximetry (although note we aren't trying to identify the difference between quantities of oxy and deoxy-haemoblobin with our device, so the difference in absorbance between these two wavelengths is a bit of a red hearing)
- https://www.slideshare.net/JefThomas1/vein-viewernir-imaging
- https://www.ncbi.nlm.nih.gov/pmc/articles/PMC5822547/
- http://www.mdpi.com/1424-8220/17/2/304/htm
- https://onlinelibrary.wiley.com/doi/abs/10.1002/lsm.10248

Will discuss further at Wednesday meeting

**Comment by chrisbodger** [comment]
Paper confirmed 850nm is optimal. See issue [44](44).

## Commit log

2018-07-30 Resource Upload
    Bring Venenfinder resources into repository
    [Cover_Venenfinder.stl, IR-Filter_MagneticClip_Venenfinder.stl, IR-LED-reflector-Matrix_Venenfinder.stl, Vene_main_case.stl]
2018-08-01 inserted more links
2018-08-08 Update CONOPS.md
    Made changes to Bill of Materials, Tools, Project Scope and Value Proposition
2018-08-13 Added Tutorial Document
    Added the initial release of the tutorial document on how to build and configure the RasPi for VeinCam. Currently only has the configuration/preparation steps, and more will be added as software beco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
    Updated the meeting minutes for the class tutorial with my input regarding the tutorial document.
2018-08-14 Added Sample Code
    For Alex to determine proper integration.
    Added more to the configuration tutorial as Wireless Hot-spotting has been achieved
2018-08-20 Renders of the Initial Case Design
2018-08-21 Create Materials Resources
2018-08-22 Case Files to be Printed
    [Casing Lid.stl, Casing Shell.stl, Casing.ipt, Casing.stl]
2018-08-22 Rename Materials Resources to Materials Resources.md
2018-08-23 Case 1.1
    Tweaked a couple things ready for open day / Audit
    [Casing Lid.stl, Casing Shell.stl]
2018-08-23 GCode for printing
2018-08-23 CAD File name adjustments
    Adjusted file names for better version tracking.
    begun alterations for version 2 of the case - to be detailed in work diary
    [Casing Lid.stl, Casing Shell.stl, Casing-Lid-v1.1.stl, Casing-Lid-v1.stl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]
2018-08-23 New Gcode for Case v1.1
    [Casing-Lid-v1.0.stl]
2018-08-23 Update Team-Work-Diary.md
    Updated Hardware regarding case printing
2018-08-23 Update Decision-Log.md
    Added more to the decision log regarding case design and LED selection
2018-08-24 Reorganised CAD folder and added minutes
    [Casing-Lid-v1.0.stl, Casing-Lid-v1.1.stl, Casing-Shell-v1.0.stl, Casing-Shell-v1.1.stl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]
2018-08-29 Case V2 drawings
    Needs GCODE conversion
    [Casing-Lid-v2.0.stl, Casing-Shell-v2.0.stl]
2018-08-29 Case V2 GCODE
    GCODE ready for print
2018-09-23 Case version upload
    Back log of case iterations
    [Casing-v2.1-shell.stl, Casing-v2.1.0003.ipt, Casing-v2.1lid.stl, Casing-v2.2 Lid.stl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]
2018-09-25 Added LED work
2018-10-02 Add files via upload
    uploaded photos of latest prototype
2018-10-02 User Manual for Prototype v2.2
2018-10-05 Update VeinCam-Tutorial.md
    Made the tutorial more comprehensive, to include the device assembly, as well as getting the software to start/autostart. Need to finalise the LED array assembly, TOC, and confirm other details with 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
2018-10-05 Update CONOPS.md
    Changes LED type in BOM back to 850nm
2018-10-06 Update Purchase-Log.md
    Added Pi Camera
2018-10-10 Final Case edits
    [button.ipt]
